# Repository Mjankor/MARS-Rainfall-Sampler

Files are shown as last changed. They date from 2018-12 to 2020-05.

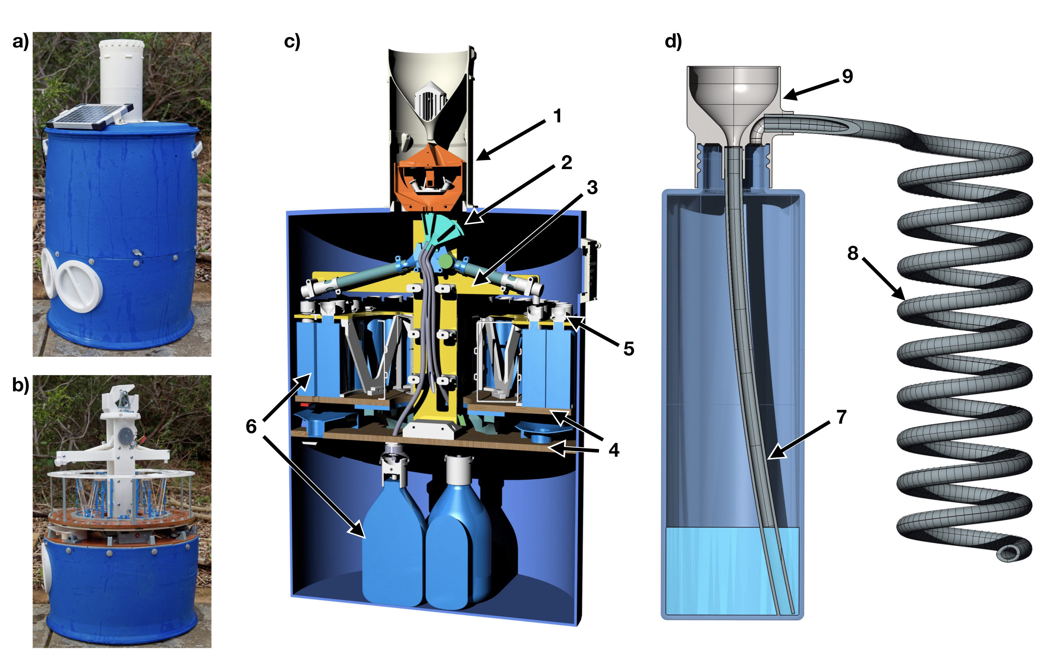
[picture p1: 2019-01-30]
Tutorial/Images/Figure 1 - 3D model and photo_colour.jpg

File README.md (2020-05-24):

# MARS-Rainfall-Sampler
A daily/monthly autonomous rainfall sampler for isotope research

Instructions for construction are being put together here:
https://cartesiancreations.dozuki.com/Guide/Guide+to+build+the+MARS+rainfall+sampler./1

If you're interested in helping, there are several things that should be improved. In particular:
1) A way to resolve the memory effect associated with the tipping bucket. Either a way to tip the bucket manually after a certain amount of time, or a way to remove the bucket entirely. 
2) A more secure method of joining the vent and inlet hoses (when using the inlet tube method). 
3) A better motor option for the main gear. The little stepper has done well so far, but something with a bit more power would be useful to make sure the turntable and platter never miss steps. Caveat - can't use much more power.

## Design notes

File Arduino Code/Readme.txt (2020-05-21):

Folder for the Arduino Code
7/10/19 - updated Arduino file to resolve undercounting in the tipping bucket. 
21/5/20 - updated Arduino file to resolve bug if the sampler runs into a 4th month sampling.

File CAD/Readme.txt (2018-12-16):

This folder contains the .STP and other cad files for the MARS rainfall sampler.

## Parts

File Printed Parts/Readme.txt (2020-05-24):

This folder contains STL files for the 3D printed components of the MARS sampler

24/5/20 - Added updated files for daily funnels, Y-junction and water switch (with prefabbed supports). These files are optimised for 3D printing.

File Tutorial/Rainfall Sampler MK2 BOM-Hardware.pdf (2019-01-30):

### Components (by category)

Hardware | Quantity | Notes
Baseplate
12mm ply baseplate | 1 sheet 1210x596 mm exterior grade or marine ply | 1
M5 x 75mm bolts | | 4 | For turntable
M5 x 35mm bolts | | 15 | For guides/brackets
M10 nuts | 3 | Cover brackets
M10 wingbolts | 3 | Upper cover
M8 x 40mm bolts | 12 | Lower cover brackets
12” Lazy susan | 1

Tower
M5 x 35mm bolts | 6 | Tower to baseplate
M5 x 75mm bolts | 14 | Tower bolts
M5 x 20mm bolts | | 4 | Y junction bolts
4g x 12mm screws | | 2 | Large gear
M3 x 20mm bolts | | 4 | Motor and microswitch bracket
M2 x 12mm bolts | | 2 | Microswitch
8mm silicone hose | 650mm long | 3 | Monthly
1m of 15mm PVC

Tipping Bucket

M3 x 20mm bolts | 4 | Support stand to baseplate
M5 x 20mm bolts | 2 | Tipping bucket adjuster screws
4G x 12mm screws | 6 | Pinions and magnet arm

Electronics
Reed switch | | 1
FE magnet (10 x 10 x 3mm) | | 1
Stepping motor and board | | 2
Arduino nano | | 1
Breakout board | | 1
DS3231 RTC | | 1
SD Card reader | | 1
Ribbon cables | 100mm or shorter | 20
Solar panel | | 1
DC Converters | 2 | 1 from 12v to Arduino, 1 from solar to battery
Reset switch | 1
M5 x 50mm bolts | 3
8g x 12mm screws | 6
4g x 12mm screws | 4 | Electronics brackets and grommet
M3 x 20mm bolts | 4 | Motor
608 bearings | 2 | Gears

Platter
Turntable | 1
M5 x 20mm bolts | 4 | Turntable attachment
7g x 20mm screws | 19 | V-brackets and support legs
8g x 12mm screws | 65 | outer and inner rim, and vent tube holders

Monthly Bottles
2L HDPE bottles | 3

Daily Bottles
225ml HDPE bottles (synergy) | 60

Outer Casing
M8 x 40mm bolts | Galvanised | 4 | Handles
M8 washers | Galvanised | 8 | Handles
M5 x 35mm bolts | Stainless | 21 | Funnel and funnel base. Portholes

Tools

### Components by quantity

Hardware | Quantity | Cost | Example
4g x 12mm screws | 12 | 4 | https://www.bunnings.com.au/zenith-4g-x-12mm-brass-countersunk-head-wood-screws-30-pack_p2420386
7g x 20mm screws | 19 | 2 | https://www.bunnings.com.au/zenith-8g-x-18mm-brass-round-head-wood-screw-10-pack_p2420389
8g x 12mm screws | 71 | 7 | https://www.bunnings.com.au/zenith-8g-x-12mm-button-head-metal-screws-100-pack_p2409525
M10 nuts | 3 | 2 | https://www.bunnings.com.au/pinnacle-m10-high-tensile-nuts-4-pack_p1101068
M10 wingbolts | 3 | 5.20 | https://www.bunnings.com.au/zenith-m10-x-25mm-zinc-plated-wing-screw-4-pack_p2420922
M2 x 12mm bolts | 2
M3 x 20mm bolts | 10 | 1 | https://core-electronics.com.au/10-sets-m3x20-screw-low-profile-hex-head-cap-screw.html
M5 x 20mm bolts | 10 | 3.30 | https://www.bunnings.com.au/pinnacle-m5-x-20mm-zinc-plated-phillips-round-head-thread-screw-10-pack_p2310475
M5 x 35mm bolts | 42 | 16.25 | https://www.bunnings.com.au/pinnacle-m5-x-40mm-zinc-plated-metal-thread-bolt-and-nut-8-pack_p2251405
M5 x 50mm bolts | 3 | 4 | https://www.bunnings.com.au/zenith-m5-x-50mm-316-stainless-steel-mushroom-head-bolt-and-nut-3-pack_p2310733
M5 x 75mm bolts | 18 | 8 | https://www.bunnings.com.au/zenith-3-16-x-75mm-zinc-plated-mushroom-head-bolt-and-nut-10-pack_p2420214
M8 x 40mm bolts | 16 | 12.65 | https://www.bunnings.com.au/zenith-m8-x-40-hex-head-hot-dip-galv-bolts-nuts_p2260551
Plywood | 1 sheet 1210x596 mm exterior grade or marine ply | 34 | https://www.bunnings.com.au/1220-x-610-x-12mm-aa-grade-mixed-hardwood-marine-plywood_p0320031
608 bearings | 2 | 7 | https://au.rs-online.com/web/p/ball-bearings/6189957/
12” Lazy susan | 1 | 18 | https://www.carbatec.com.au/hardware-and-project-supplies/project-kits/lazy-susan-bearing-12
15mm pvc | 1 | 2.20 | https://www.bunnings.com.au/holman-15mm-x-1m-class-18-pvc-pipe_p4750046
200L plastic drum | 1 | 33 | https://www.gumtree.com.au/s-ad/dry-creek/miscellaneous-goods/drum-and-ibc-parts-and-accessories-for-sale/1056426496
Varnish | 1 | 10 | https://www.bunnings.com.au/bondall-250ml-gloss-monocel-clear-timber-varnish_p1520507
169.6
Electronics
Reed switch | 1 | 2 | https://www.jaycar.com.au/glass-reed-switch-n-o/p/SM1002
FE magnet (10 x 10 x 3mm) | 1 | 2 | https://www.jaycar.com.au/ferrite-magnets-pk-12/p/LM1616

Stepping motor and board
| 2 | 20 | https://www.jaycar.com.au/arduino-compatible-5v-stepper-motor-with-controller/p/XC4458
Arduino nano | 1 | 15 | https://core-electronics.com.au/nano-v3-0-board-arduino-nano-v3-0-compatible.html
Breakout board | 1 | 12 | https://www.ebay.com.au/itm/Arduino-Nano-Uno-R3-Mega328-Expansion-Breakout-Board-Shield/291691880760?hash=item43ea30e138:g:iNUAAOSwez5ZvQet
DS3231 RTC | 1 | 4 | http://www.ebay.com.au/itm/Real-Time-Clock-Memory-Module-For-Arduino-DS3231-AT24C32-IIC-I2C-Precision/173037140776?hash=item2849d13b28:g:UTIAAOSwytJaL9~U
SD Card reader | 1 | 3 | https://www.ebay.com.au/itm/2pcs-SD-Card-Module-Slot-Socket-Reader-Read-Write-ARM-MCU-MP3-16-Pin-Arduino/152681876599?hash=item238c8c8c77:g:TacAAOSwI-BWH15f
Ribbon cables | 20 | 3.50 | https://core-electronics.com.au/premium-female-female-jumper-wires-20-x-3-75mm.html
Solar panel | 1 | 23 | https://www.jaycar.com.au/powertech-monocrystalline-solar-panel-5w/p/ZM9091
DC Converters | 2 | 7 | https://www.ebay.com.au/itm/2pcs-3A-DC-DC-Adjustable-Power-Supply-Module-Variable-PSU-RC-Plane-LM2596-MP1584/162001945475?ssPageName=STRK%3AMEBIDX%3AIT&_trksid=p2060353.m2749.l2649
Battery | 1 | 24 | https://www.jaycar.com.au/search?text=12v+battery&CSRFToken=b78e4751-c07c-409b-9efc-f15883b63a5d
Reset Switch | 1 | 2 | https://www.jaycar.com.au/pushbutton-push-o
Wires | | 5 | https://www.jaycar.com.au/hook-up-wire-pack-2-metres/p/WH3025
| | 122.5
Laser Cutting
Tower, platter, V- braces, gears. 6mm acrylic | 3 | 75 | FabLab prices for 3 sheets of 600x400x6mm
| | 75
3D Printing
ABS | 2 spools | 40
PETG | 1 spool | 40
ASA | 1 spool | 40
| | 120
Bottles
Vent tubes | 135m | 65 | https://www.bunnings.com.au/holman-4mm-x-25m-irrigation-drip-tube-riser_p3120591
| | 65
Bottles 225ml | 60 | 30
Bottles 2L | 3 | 15
Total
Build | | 552.1
Bottles | | 45

1

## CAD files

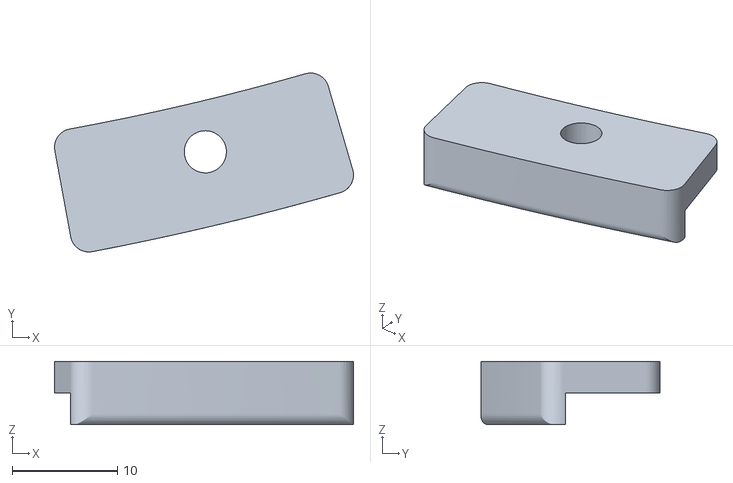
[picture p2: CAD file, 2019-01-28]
Printed Parts/Platter/Mk2 Small main gear spacer.stl
28.4 x 17.0 x 6.00

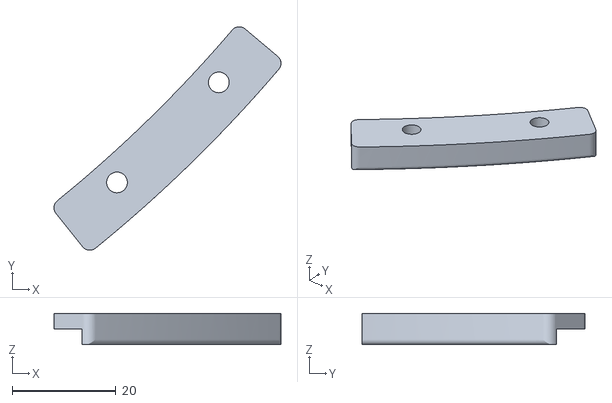
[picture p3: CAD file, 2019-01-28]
Printed Parts/Platter/Mk2 Large main gear spacer.stl
43.8 x 43.1 x 6.00

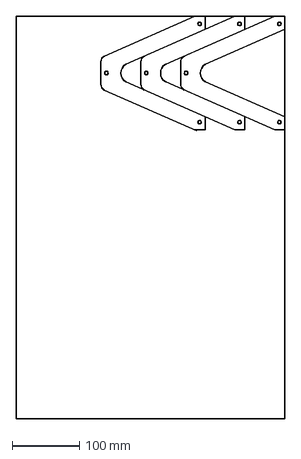
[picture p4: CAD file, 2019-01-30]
Laser Cutting templates/Platter and Tower_6mm Acrylic Sheet3.dxf
400.0 x 600.0 mm

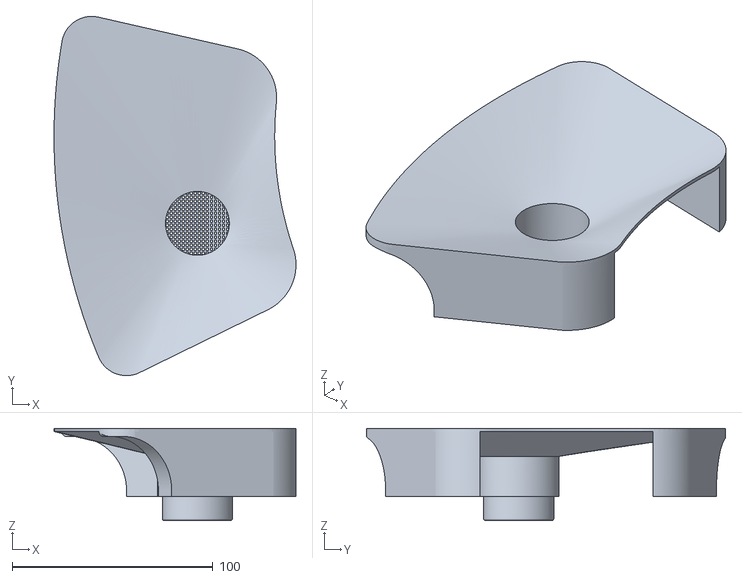
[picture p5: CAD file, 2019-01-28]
Printed Parts/Baseplate/Mk2 Drain 2.stl
120.6 x 179.0 x 46.0

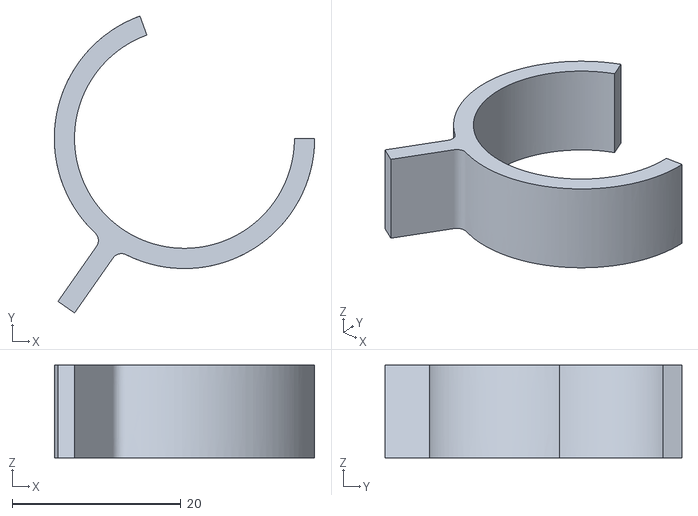
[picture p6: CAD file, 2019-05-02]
Printed Parts/Bottle caps/Bottle Clamp.stl
30.9 x 35.2 x 11.0

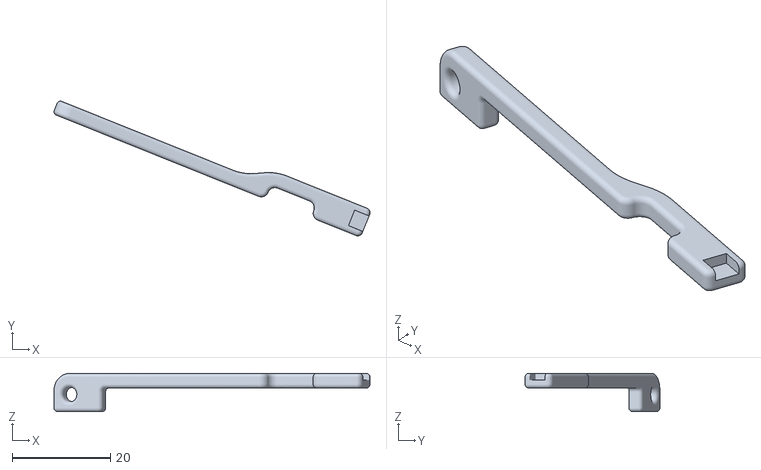
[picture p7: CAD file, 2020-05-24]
Printed Parts/Electronics/Mk2 Arduino clamping arm.stl
64.3 x 27.4 x 7.80

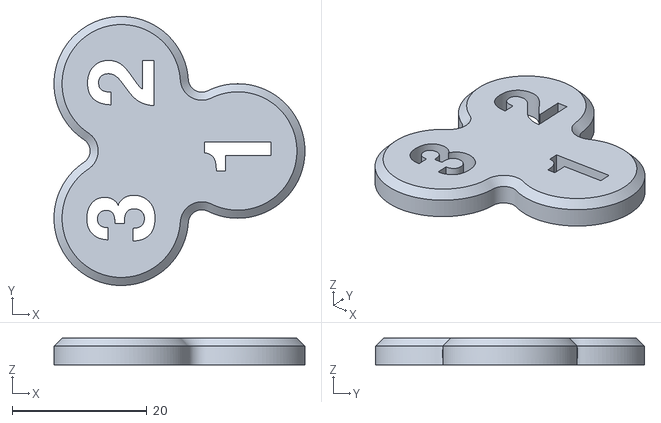
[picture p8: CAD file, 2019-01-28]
Printed Parts/Platter/Monthly Reminder tag.stl
37.3 x 40.0 x 4.00

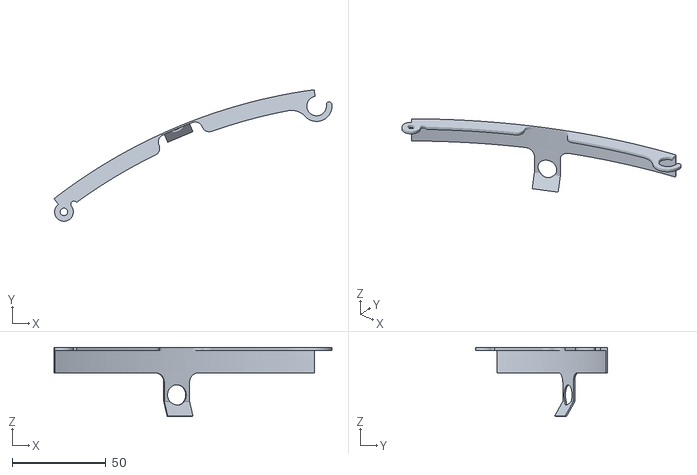
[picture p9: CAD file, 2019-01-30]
Printed Parts/Shims/Shim_small.stl
148.1 x 70.1 x 36.8

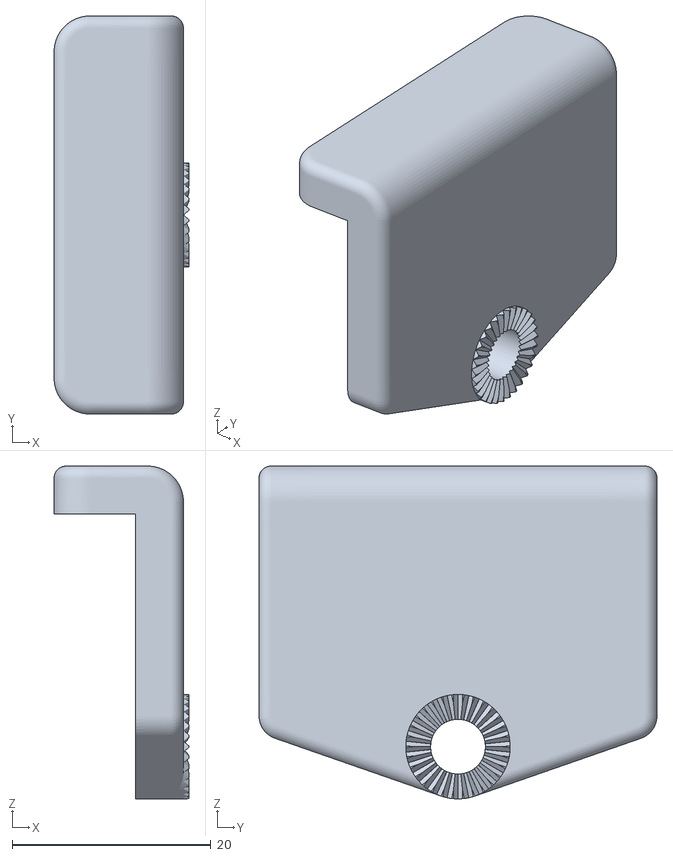
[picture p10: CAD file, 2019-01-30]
Printed Parts/Solar Panel Holder/Solar panel clamp 2.stl
13.5 x 40.0 x 33.5

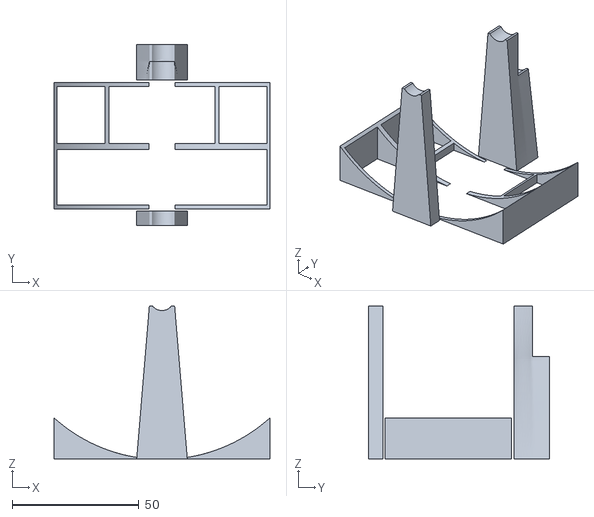
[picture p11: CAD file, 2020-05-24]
Printed Parts/Tipping Bucket/Tipping Bucket mk3_switch supports.stl
85.3 x 71.7 x 60.3

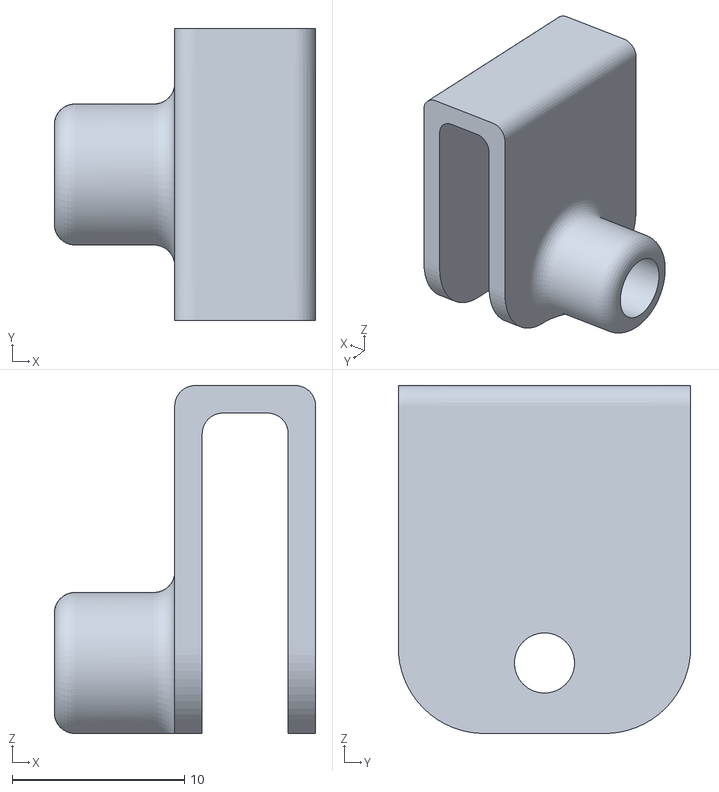
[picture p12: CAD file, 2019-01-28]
Printed Parts/Tools/Drillguide.stl
15.2 x 17.0 x 20.2

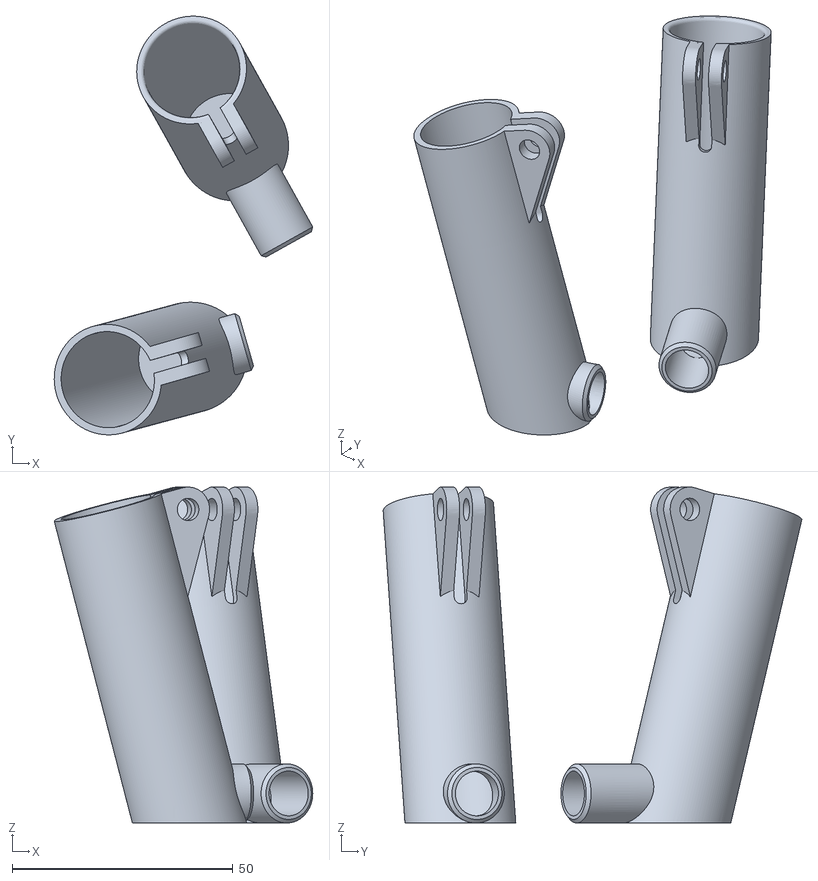
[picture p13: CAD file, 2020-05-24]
Printed Parts/Tower/Mk2 Daily funnels.stl
58.5 x 94.8 x 76.1

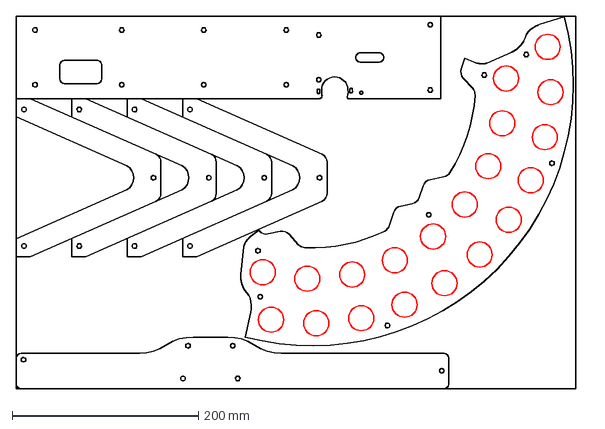
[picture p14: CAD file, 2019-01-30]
Laser Cutting templates/Platter and Tower_6mm Acrylic Sheet1.dxf
613.7 x 400.0 mm

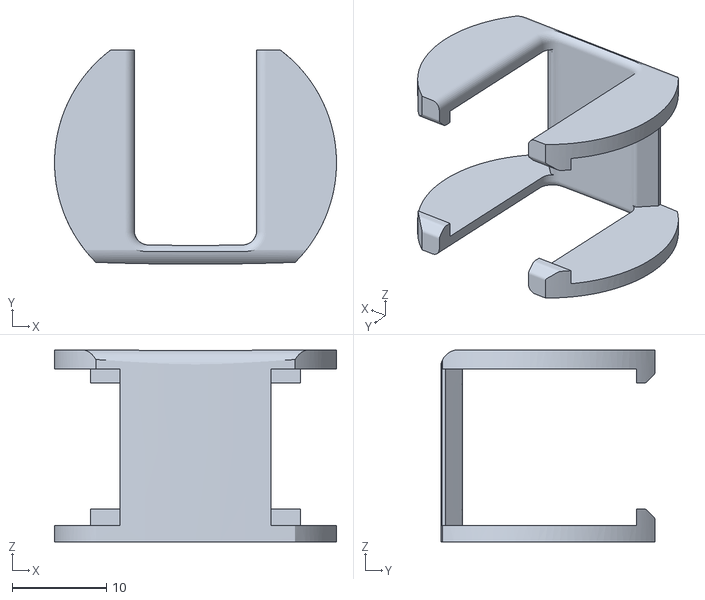
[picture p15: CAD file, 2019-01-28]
Printed Parts/Baseplate/Mk2 Grommet_1.stl
30.0 x 22.8 x 20.4

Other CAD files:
Printed Parts/Bottle caps/Mk2 Bottleclamp.stl
Printed Parts/Electronics/Mk2 Motor support arm.stl
Printed Parts/Shims/Shim_large.stl
Printed Parts/Solar Panel Holder/Solar panel clamp 3.stl
Laser Cutting templates/Platter and Tower_6mm Acrylic Sheet2.dxf
Printed Parts/Baseplate/Mk2 Cover clamps.stl
Printed Parts/Baseplate/Mk2 Cover guides.stl
Printed Parts/Baseplate/Mk2 Grommet_2.stl
Printed Parts/Baseplate/Mk2 TurntableSupport.stl
Printed Parts/Baseplate/Mk2 lower clamp.stl
Printed Parts/Baseplate/Mk2 lower legs.stl
Printed Parts/Bottle caps/2 litre bottle cap Aqua systems - funnel.stl
Printed Parts/Bottle caps/Bottle Funnel mk2.stl
Printed Parts/Bottle caps/Mk2 Bottleclamp screwthread.stl
Printed Parts/Bottle caps/Mk2 Hoseclamp inner.stl
Printed Parts/Bottle caps/Mk2 Hoseclamp outer.stl
Printed Parts/Electronics/Mk2 DC Converter box.stl
Printed Parts/Electronics/Mk2 Motor support.stl
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

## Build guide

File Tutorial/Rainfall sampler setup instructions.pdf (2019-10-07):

Rainfall sampler initial setup

1) Find a level patch of ground and place the sampler in position.
2) Unplug the solar panel and remove the sampler lid (3 wing bolts at the base of the lid).

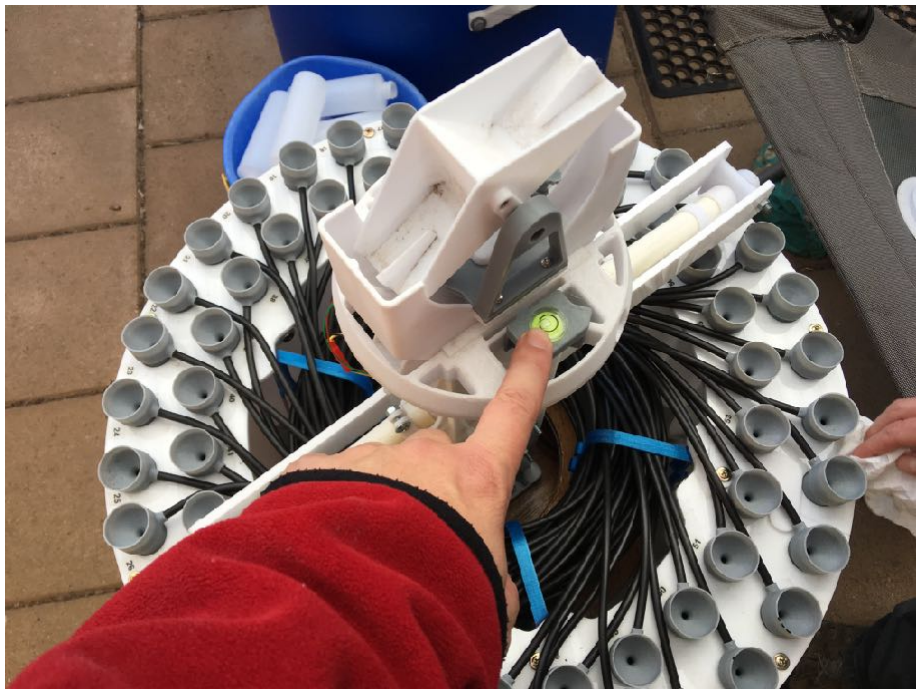
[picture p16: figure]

3) Make sure the sampler is level using the level bubble mounted by the tipping bucket
4) Place any weights you wish in the base of the sampler. I usually use half a dozen bricks in case of windy conditions. Place them around the outer edge so there’s room for the monthly bottles.
5) Place the battery in its bay (if not already in place) and plug it in.
6) Check the the power/USB cable is plugged into the control box.

As soon as power is plugged in, the sampler will start its power-up routine, so depending on what state the sampler is in, a few things may move. The platter may rotate back and forth one bottle, and the water switch may move. There’s still a few things to check before it’s ready to go, so don’t worry about that yet.

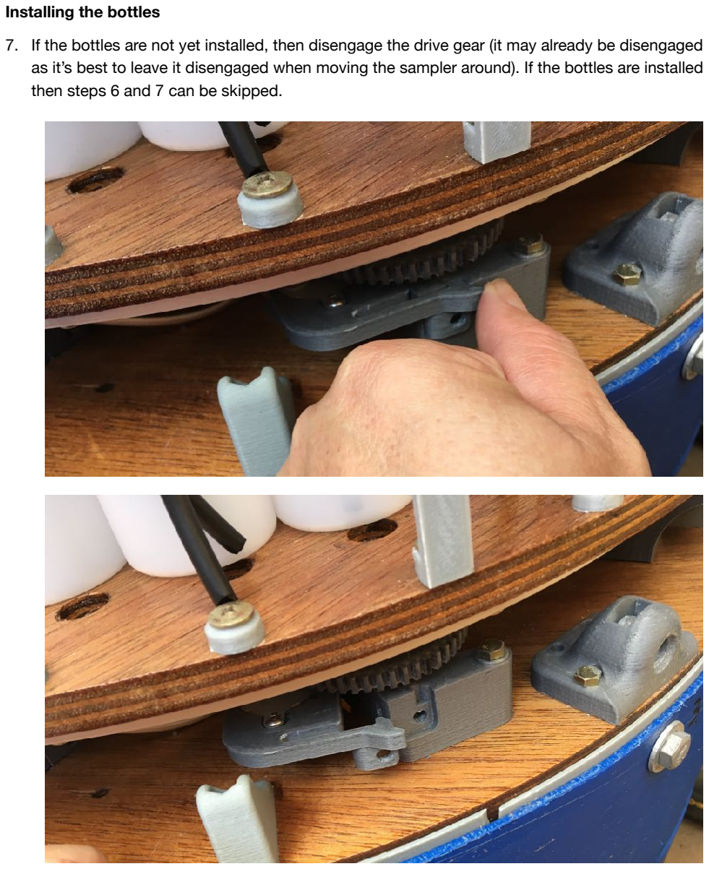
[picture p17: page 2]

Installing the bottles

7. If the bottles are not yet installed, then disengage the drive gear (it may already be disengaged as it’s best to leave it disengaged when moving the sampler around). If the bottles are installed then steps 6 and 7 can be skipped.

8. Install each bottle. Ensure they are firmly screwed onto each cap, but don’t use excessive force, otherwise you can break the bottlecaps. As you install each bottle, add a ‘hold-down’ clamp so that the bottles and bottlecaps can’t pop up and jam the sampler.

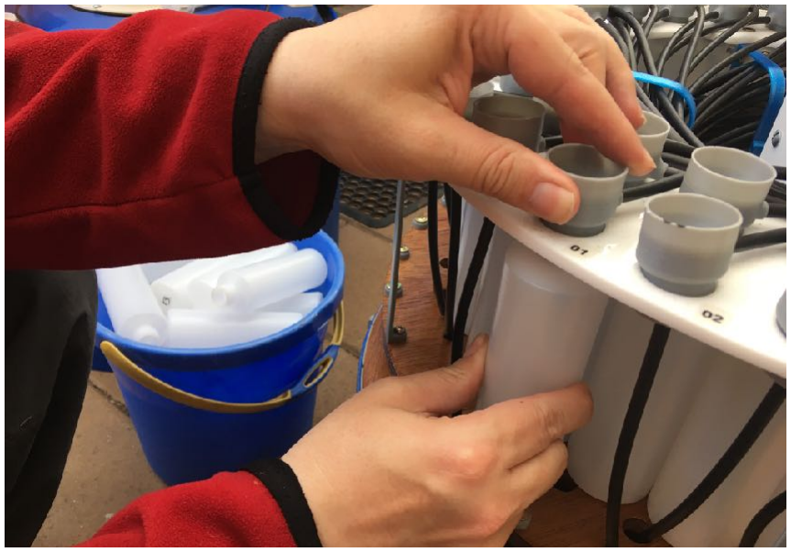
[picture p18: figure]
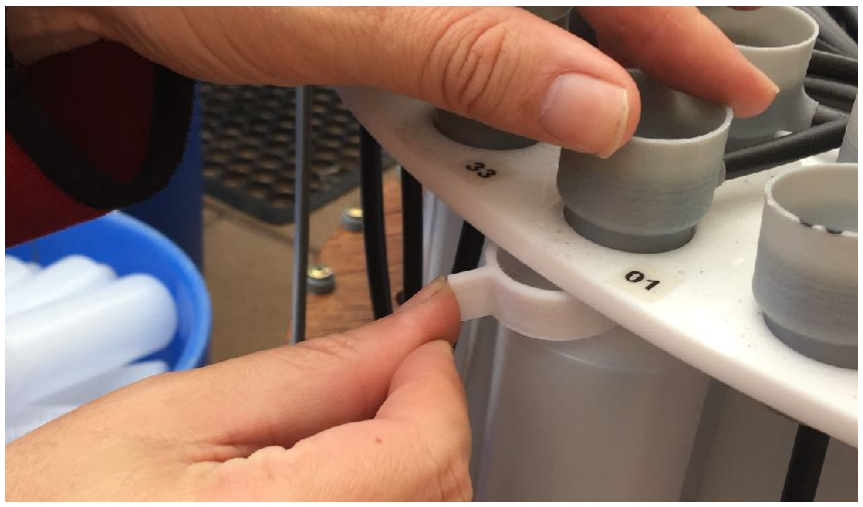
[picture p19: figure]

9. Once all the bottles are installed, then re-engage the drive gear.
10. Install the monthly bottles. Each monthly bottle has a cap with a short tube, connected via a tube connector to a coiled tube in the base of the sampler. There are clips on the plywood roof of the base compartment that will align each monthly bottle with its inlet hose.

Prestart Checks

The sampler should now be setup, with all bottles in place, and power connected. The next step is to make sure it’s ready to run.

11. Disengage the gear and rotate the daily bottle platter until sample #1 is aligned with the outer daily water tube. As you do this, double check that all the ‘hold down’ clips are installed and that no bottle caps are sitting high.
12. Re-engage the gear.
13. Check the SD card is installed.
14. Press the red reset button on the control box. This will restart the sampler and run some simple checks. The main bottle platter will rotate backwards one bottle, then forwards back to sample #1. This checks that there is sufficient power to turn the platter and that nothing is jamming it. Then, the water switch will rotate into its first position (Sitting against the microswitch).

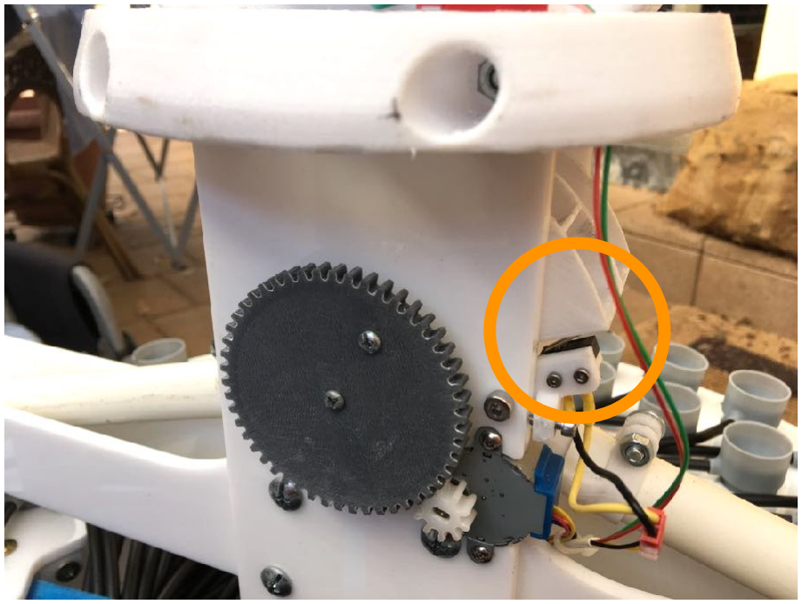
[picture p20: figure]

15. If the water switch doesn’t settle against the microswitch, instead rotating back and forth once and settling on the other side, this means that the SD Card can’t be initialised. If the water switch rotates back and forth twice, then it means the SD card was initialised but there is a problem creating the log file.

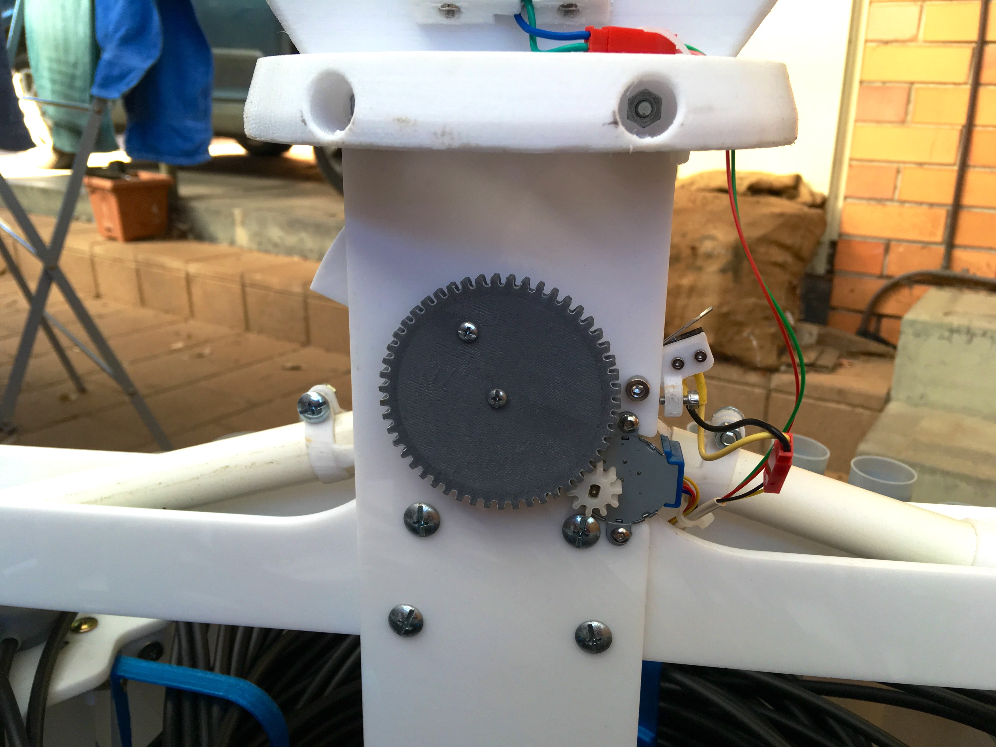
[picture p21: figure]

16. Assuming the sampler passed its checks, then place the lid back on the sampler. Be careful to avoid hitting the tower and tipping bucket as you lower it. Secure it with the wing-bolts.
17. Re-attach the solar panel cable.
18. If necessary, install the funnel, bird spikes and filter.

Sampling Considerations

The sampler can collect up to 60 days of rainfall over 3 months. However, there are a few scenarios where fewer bottles may be collected.

Each bottle holds 225ml, or around 22mm of rainfall. In the case of significant weather events greater than this amount, the sample may be split across multiple bottles.

The water switch has four positions.
1 = outer daily ring, and month 1

2 = outer daily ring and month 2

3 = inner daily ring and month 2
4 = inner daily ring and month 3

This mechanical configuration means that only 27 bottles are available during month 3, and 33 bottles are available for month 1. This should not usually be a problem, but it’s worth keeping an eye on anticipated rainfall in case a series of large events occur during a single month.

Replacing bottles

1. Unplug solar panel and remove the sampler lid.
2. Disengage drive gear
3. Eject SD card and copy data to computer
4. Remove ‘hold-down’ clips and remove and label daily bottles.
5. Install replacement bottles and reinstall clips
6. Disconnect monthly bottles from tube via quick release connectors, remove bottle from central holding clip and carefully remove and label.
7. Install replacement monthly bottles
8. Replace SD card
9. Reset the platter so sample #1 is under the outer ring’s daily water tube.
10. Press the reset button and confirm that sampler has passed prestart checks.
11. Replace lid and re-connect solar panel.

*A note on the SD card logging.
At 9 am on each day the sampler will log the information for the previous day, consisting of the collection end date&time and number of tips recorded. In the next line, it will record the active sample ID and the water switch position for the new day to the card.

This may be somewhat confusing at first glance, because it means that the actual data logged for each day begins in the middle of each line. However, doing the logging in this fashion means that all data is logged as necessary and the machine is more resilient to power failure. It also means that a sample ID will often show up on multiple lines. Each day the sampler will test if sufficient tips have occurred (usually > 2) and only if that is the case will it rotate to a new sample. We record the log every day as a useful diagnostic in case anything goes awry with the sampler. This means that it’s quite common for a sample to show up on many lines, until it has registered enough tips and the rotation to a new sample has occurred.

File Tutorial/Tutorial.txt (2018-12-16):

Not ready yet, but this folder will contain the construction tutorial.

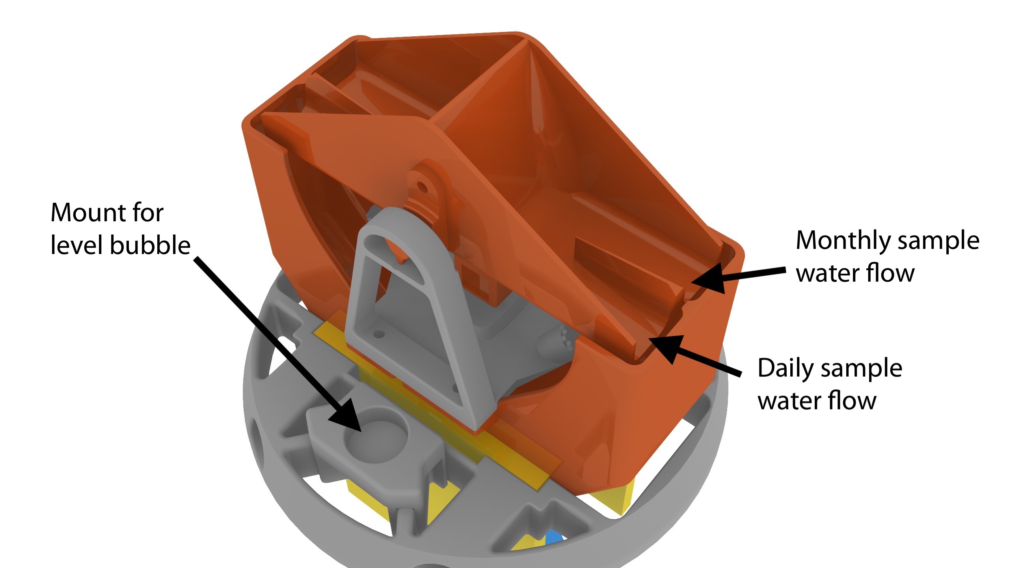
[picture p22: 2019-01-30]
Tutorial/Images/Figure 2 - Tipping Bucket_colour.jpeg

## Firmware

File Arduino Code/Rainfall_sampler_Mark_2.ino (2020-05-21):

#include <BlockDriver.h>
#include <FreeStack.h>
#include <MinimumSerial.h>
#include <SdFat.h>
#include <SdFatConfig.h>
#include <SysCall.h>
#include <Wire.h>
#include <RTClib.h>
#include <SPI.h>
#include <AccelStepper.h>
#include <avr/wdt.h>            // library for default watchdog functions
#include <avr/interrupt.h>      // library for interrupts handling
#include <avr/sleep.h>          // library for sleep
#include <avr/power.h>          // library for power control
//Watchdog code modified from http://folk.uio.no/jeanra/Microelectronics/ArduinoWatchdog.html

//setup global variables
//pins used are D3/D4/D5/D6 = stepper, A0 (14) = servo, A4 and A5 (18,19) = RTC, D10,D11,D12,D13 = SDcard. update this.
//Motor code from http://42bots.com/tutorials/28byj-48-stepper-motor-with-uln2003-driver-and-arduino-uno/
#define HALFSTEP 8
#define FULLSTEP 4
#define motorPin1  A3     // IN1 on the ULN2003 driver 1
#define motorPin2  A2     // IN2 on the ULN2003 driver 1
#define motorPin3  A1     // IN3 on the ULN2003 driver 1
#define motorPin4  A0     // IN4 on the ULN2003 driver 1
#define switchmotorPin1  6     // IN1 on the ULN2003 driver 1
#define switchmotorPin2  7     // IN2 on the ULN2003 driver 1
#define switchmotorPin3  8     // IN3 on the ULN2003 driver 1
#define switchmotorPin4  9     // IN4 on the ULN2003 driver 1

//SD Card, motor and clock variables
SdFat SD;
File Logfile;
int pinCS = 10;
AccelStepper bottlestepper(FULLSTEP, motorPin1, motorPin3, motorPin2, motorPin4);
AccelStepper switchstepper(FULLSTEP, switchmotorPin1, switchmotorPin3, switchmotorPin2, switchmotorPin4);
RTC_DS3231  rtc;
//char daysOfTheWeek[7][12] = {"Sunday", "Monday", "Tuesday", "Wednesday", "Thursday", "Friday", "Saturday"};

//*****************
//General variables
//*****************
boolean sampleRunComplete =false;
byte sampleCounter = 1; // used to set the initial sampler ID. Could change if you want to start at some other ID.
byte activeDay;
int startMonth;
byte sampletime = 9; // Change this to the hour you want the new sample to begin (typically 9 am)(24hour time).
byte monthFuzzyStart = 25; //Change this depending on how much slop you want at the start of each month. eg: you may setup the sampler on the 27th due to logistics, but don't want that month to only collect from the 27th to 30th)
//Platter rotation variables
short outersteps = 3105; //adjust value to tweak outer ring sample steps. //first calc was 3088
short innersteps =  3795; //adjust value to tweak inner ring sample steps. //first calc was 3774
short changeoversteps = 350; //-4500; //adjust value to tweak changeover from outer to inner sample ring. (note. Goes the opposite way to the inner and outersteps).
//Water switch adjustment variables
short position1 = 50; //Should be 0. This is the starting position for the water switch
short position2 = 650; //Second position - adjust to align so waterswitch fills outer ring and month 2
short position3 = 1300; //Third position - adjust to align so waterswitch fills inner ring and month 2
short position4 = 1900; //Fourth position - adjust to align so waterswitch fills inner ring and month 3.
byte resetswitchpin = 3;
bool resettoggle = HIGH;//tipping bucket variables
// Tipping bucket sensor variables
const byte interruptsensor = 2;
volatile int tipcounter = 0; 
long debounceInterval = 50000; //Debouncing Time in microseconds
volatile unsigned long last_micros = 0;
volatile bool BucketTipped = false;
short tips = 0; //used in tippingSensorCheck
//int debounceInterval = 50;
short maxtipcount = 100;// 50; //Determine how many tips are allowed if using a tipping bucket sensor. eg: 10mm of rain per bottle, as 0.2mm per tip = 50.
//add servomax and servo min angles here for easy configuration.
short mintipcount = 2; // Used to provide a buffer in case of tiny rainfall amounts, morning dew, etc. 0 means it will start a new sample with even a single tip. 3 means it requires 3 tips to qualify as a new sample. 

//*****************
void setup() {
//*****************
//Setup serial output for monitoring.
 delay (3000); //wait 3 seconds for terminal to wake up.
//  Serial.begin(115200); //remove post debug
    Serial.println(F("MARS-02 activated."));

//Setup tipping bucket sensor
  pinMode(interruptsensor, INPUT_PULLUP);
  attachInterrupt(digitalPinToInterrupt(interruptsensor), tipinterrupt, FALLING);
  tipcounter = 0;

// configure the watchdog 
  configure_wdt();

//Setup RTC
    if (! rtc.begin()) {
      Serial.println(F("Couldn't find RTC"));
      while (1);
    }
   //rtc.adjust(DateTime(F(__DATE__), F(__TIME__))); //use to force an RTC correction. Comment out after use.
if (rtc.lostPower()) {
    Serial.println(F("RTC lost power, lets set the time!"));
    // following line sets the RTC to the date & time this sketch was compiled
    rtc.adjust(DateTime(2000, 1, 1, 0, 0, 0));
    //This line sets the RTC with an explicit date & time, for example to set
    //January 21, 2014 at 3am you would call:
    //rtc.adjust(DateTime(2014, 1, 21, 3, 0, 0));
} //end RTC
     DateTime Timestamp = rtc.now();
     Serial.print(F("Current time: ")); //remove serial output post debug
     Serial.print(Timestamp.day(), DEC);
     Serial.print("/");
     Serial.print(Timestamp.month(), DEC);
     Serial.print("/");
     Serial.print(Timestamp.year(), DEC);
     Serial.print("\t");     
     Serial.print(Timestamp.hour(), DEC);
     Serial.print(":");
     Serial.print(Timestamp.minute(), DEC);
     Serial.print(":");
     Serial.print(Timestamp.second(), DEC);
     Serial.println(F("\t(DD/MM/YY HH:MM:SS)"));

//set the starting month (with some fuzziness in case the sampler is setup early)
setStartMonth();

monthDelta();

//setup parameters for the stepper motors
  switchstepper.setMaxSpeed(500);
  switchstepper.setAcceleration(50.0);
  switchstepper.setSpeed (-300);
  bottlestepper.setMaxSpeed(1000);
  bottlestepper.setAcceleration(100.0);

//and the microswitch
  pinMode(resetswitchpin, INPUT_PULLUP);
  
  BottleOACW(); //test back and forth movement
  BottleOCW();
  Serial.println(F("MARS-01 bottlestepper activated."));

  //Here we need it to call the reset function for the water switch
  resetwaterswitch();
  waterSwitchPos(1); //reset to position 1.
  Serial.println(F("Water switch reset to starting position"));

//Setup the SD card. Make sure you disable the stepper motors before trying to setup the card, otherwise it will fail (guessing too much power usage).
  pinMode(pinCS, OUTPUT);
  digitalWrite(10, HIGH);
    if (SD.begin())
  {
    Serial.println(F("SD card is ready to use."));
  } else
  {
    Serial.println(F("SD card initialization failed"));
  waterSwitchPos(4);
  waterSwitchPos(1);
  waterSwitchPos(4);
    return;
  }
  
  // Create/Open file 
  Logfile = SD.open("MARS-01.txt", FILE_WRITE);
     if (Logfile){
     DateTime Timestamp = rtc.now();
     Serial.print(F("New sample run commenced on: "));
     Serial.print(Timestamp.day(), DEC);
     Serial.print("/");
     Serial.print(Timestamp.month(), DEC);
     Serial.print("/");
     Serial.print(Timestamp.year(), DEC);
     Serial.print(" ");     
     Serial.print(Timestamp.hour(), DEC);
     Serial.print(":");
     Serial.print(Timestamp.minute(), DEC);
     Serial.print(":");
     Serial.print(Timestamp.second(), DEC);
     Serial.println(F("\t(DD/MM/YY HH:MM:SS)"));
     Logfile.println();
     Logfile.print(F("New sample run commenced on: "));
     format (Timestamp.day());
     Logfile.print("/");
     format (Timestamp.month());
     Logfile.print("/");
     format (Timestamp.year());
     Logfile.print("\t");     
     format (Timestamp.hour());
     Logfile.print(":");
     format (Timestamp.minute());
     Logfile.print(":");
     format (Timestamp.second());
     Logfile.println(F("\t(Date Format: DD/MM/YY HH:MM:SS)"));
     Logfile.println("Sample ID\tWater Switch Position\tCollection start date&time\tCollection end date&time\tTipping count\tAverage Temperature\tAverage Humidity");
     Logfile.close();
     } else {
  // We need a way to alert to SD card errors. What we'll do is toggle the water switch 3 times if the SD card doesn't work
  waterSwitchPos(4);
  waterSwitchPos(1);
  waterSwitchPos(4);
  waterSwitchPos(1);
  waterSwitchPos(4);
     }

// Record the day for the first sample.
     SD.begin();
     Logfile = SD.open("MARS-01.txt", FILE_WRITE);
     Logfile.print("Sample: ");
     Logfile.print(sampleCounter);
     Logfile.print ("\t");
     Logfile.print (waterSwitchCheck());
     Logfile.print("\t");
     format(Timestamp.day());
     Logfile.print("/");
     format (Timestamp.month());
     Logfile.print("/");
     format (Timestamp.year());
     Logfile.print(" ");     
     format (Timestamp.hour());
     Logfile.print(":");
     format (Timestamp.minute());
     Logfile.print(":");
     format (Timestamp.second());
     Logfile.print(F("\t"));
     Logfile.close(); //leaves line open for completion with the next record.

// And note the active day
activeDay = currentDay();
monthDelta();
Serial.println("Setup complete");
}//end setup

//*****************
//Custom functions
//*****************
//****Watchdog interrupt
//Setup interrupt so the watchdog can wake up the Arduino.
ISR(WDT_vect)
{
       wdt_reset();
}

// function to configure the watchdog: let it sleep 8 seconds before firing
// when firing, configure it for resuming program execution by default.
void configure_wdt(void)
{
  cli();                           // disable interrupts for changing the registers
  MCUSR = 0;                       // reset status register flags
                                   // Put timer in interrupt-only mode:                                       
  WDTCSR |= 0b00011000;            // Set WDCE (5th from left) and WDE (4th from left) to enter config mode,
                                   // using bitwise OR assignment (leaves other bits unchanged).
  WDTCSR =  0b01000000 | 0b100001; // set WDIE: interrupt enabled (8 seconds)
  //  WDTCSR =  0b01000000 | 0b000000; // set WDIE: interrupt enabled (1 second)
                                   // clr WDE: reset disabled
                                   // and set delay interval (right side of bar) to 8 seconds
  sei();                           // re-enable interrupts 
  // reminder of the definitions for the time before firing
  // delay interval patterns:
  //  16 ms:     0b000000
  //  500 ms:    0b000101
  //  1 second:  0b000110
  //  2 seconds: 0b000111
  //  4 seconds: 0b100000
  //  8 seconds: 0b100001
}

// Put the Arduino to deep sleep. Only an interrupt can wake it up.
void sleep(int sleepcycles) {  
  // Set sleep to full power down.  Only external interrupts or
  // the watchdog timer can wake the CPU!
  set_sleep_mode(SLEEP_MODE_PWR_DOWN);
  // Turn off the ADC while asleep.
  power_adc_disable();
  while (sleepcycles > 0){ // while some cycles left, sleep!
  // Enable sleep and enter sleep mode.
  sleep_mode();
  // CPU is now asleep and program execution completely halts!
  // Once awake, execution will resume at this point if the
  // watchdog is configured for resume rather than restart 
  // When awake, disable sleep mode
  sleep_disable();
    if (BucketTipped == true){
      tipcounter++;
      BucketTipped = false;
    }
  sleepcycles--;
  }
 // put everything on again
  power_all_enable();
}

//****Tipping bucket counter
//counter that the tipping bucket can increment using interrupts.
void tipinterrupt(){
//static unsigned long last_interrupt_time = 0;
    //if ((long)(micros() - last_micros) >= debounceInterval){
    BucketTipped = true;
    //last_micros = micros();
    //}
}

void tippingSensorCheck(){
  if (tips != tipcounter){
    Serial.print(F("Tipcounter tips: "));
    Serial.println (tipcounter);
    //Serial.println(last_micros);
    tips = tipcounter;
  }
}
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

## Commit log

2019-01-28 Add files via upload
    Arduino code for rainfall sampler. Currently setup for daily and monthly sampling.
2019-02-06 Add files via upload
    Complete .step files for the rainfall sampler Mk2.
2019-05-02 Add files via upload
    Bottle clamp - used to prevent bottles lifting to far above the platter surface and hitting the outlet pipes.
    [Bottle Clamp.stl]
2020-11-01 Add files via upload
    Libraries used by CHIMBLE sampler (as well as a few others). Note, some of these may be older than current versions.
